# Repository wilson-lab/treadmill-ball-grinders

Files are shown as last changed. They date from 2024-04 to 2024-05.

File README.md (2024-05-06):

Treadmill Ball Grinders
===

**In progress: versioned documentation for ease of sharing.**

## Spherical Treadmill Fabrication

### Materials
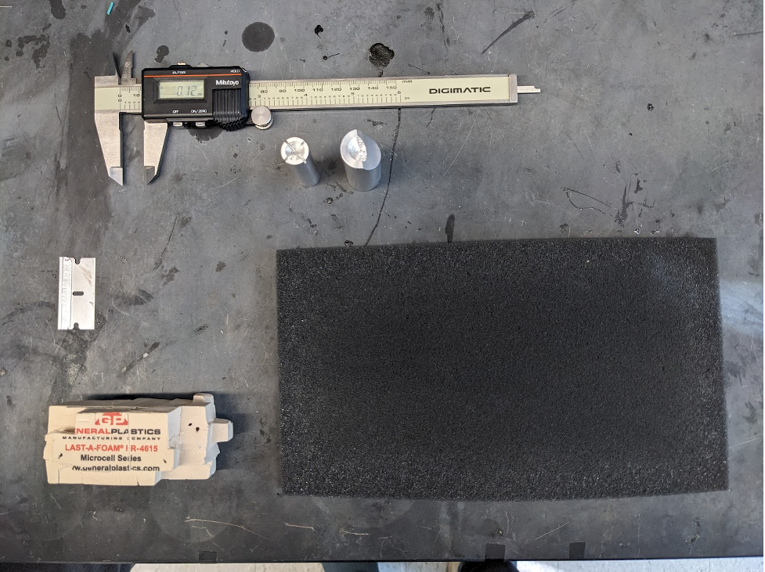
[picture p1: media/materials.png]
materials

* Foam - FR-4615 from General plastics
* Razor blade
* 'Coarse' and 'fine' foam sphere grinders
* Calipers capable of tenths of milimeters
* Soft foam pad
* Ball holder and air regulator
* Black paint or a paint pen (optional)
* Snugly fitting gloves (optional)
* Face mask (optional)

### Notes
* Wearing gloves can be helpful to avoid pressing oils from your fingers into the ball, which make the ball harder to grind.
* Wear a face mask to avoid breathing in the dust as you grind, and wipe up excess foam afterwards.

### Fabrication Steps
1. **Cut a cube foam starting matrial.** Cut a cube (carefully) of the FR-4615 foam that is around ~11mm on each side using a razor blade.
	* It can be helpful to mark out the edges with a fine-tipped marker first, then cut into them (the marks will be ground away before the end).
1. **Trim the cube of foam.** Using the razor blade, trim down the sharp edges and corners of the cube to make it more spherical (e.g. the way you might peel a grapefruit's skin). 
	* Doing more of this trimming into a spherical shape here will make the next step easier. You should get a sense for it as you try the next step if you’ve done enough.
1. **Begin grinding the trimmed cube.** Place the trimmed material into the coarse (bigger) grinder that has a diameter of ~11.5 mm and start grinding down the cube. To do this:
	* Place the ball in the “cup" of the grinder and then grind it down by rolling it “away” from you with your thumb and forefinger. Apply enough force for the grooves in the cup to cut away the edges of the ball.
	* The initial grinds as the cube molds into a sphere require more force, and you will notice big chunks chipping off the foam.
	* You can roll it a bit to remove material, then take it out, rotate it a bit, and do it again on another face. It will eventually become much easier to move as it becomes more sphere-like. 
	* As the cube transforms into a sphere, use gentle force to avoid big chips that can leave deep dents or compress the foam.
	* Continue massaging the ball into the metal grinder while continuously moving the ball around to allow for all surfaces to get shaved down evenly. Keep doing this until hardly any material is being taken away and the ball appears smooth.
	* You’ll need to periodically knock the dust out of the grinder, so it ends up being: roll a bit, knock out the dust, rotate ball position, roll a bit… and so on.
1. **Grind the sphere to near its target size.** Move to the smaller spherical grinder when the ball is ~9.2 mm diameter and fits into the fine (smaller) grinder. 
	* Continue massaging the ball to allow for even shaving across the entire surface of the sphere. 
	* When the ball is close to its final size, switch to rolling the ball around on the surface of the soft foam pad. Keep the ball secured in the metal grinder, but be careful, the ball may jump off the foam. Note this step is to help ensure the ball finishes with very even shaving.
1. **Test ball performance as you finish grinding**. As the ball gets closer to 9mm start putting the ball on the ball holder with ~50-100mL/min of air and watching its behavior. 
	* The final diameter of the ball is ~9mm, _but we recommend starting to test when it is slightly larger to avoid overshooting._ 
	* Guidelines for what to look for when the ball is levitating on the air cushion:
		* The ball should fit snugly in the ball holder and bob gently.
		* The ball should not wobble from side to side, this indicates the ball is too small.
		* The ball should spin freely in circles when nudged with a feather, this indicates there is no friction from the holder.
	* The ball might pass all the check points, but ultimately the flies must decide if they like it or not.
1. **(optional) Add markings to the ball for tracking** Once the ball is the final desired size, use the black acrylic paint or paint pen to mark the surface of the ball for behavioral tracking (e.g. a camera and FicTrac)
	* Ensure that every view angle of the ball has a unique pattern on it.
	* Numbers and letters are generally good, or spots of different sizes and shapes. 
	* Sharpie will also work for marking the ball but will have much less contrast under IR compared to the black paint. 
	* NOTE: if you grind the ball down after applying the markings, you will smear them and reduce the contrast.

## Grinders

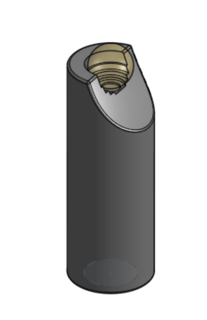
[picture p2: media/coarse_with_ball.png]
coarse


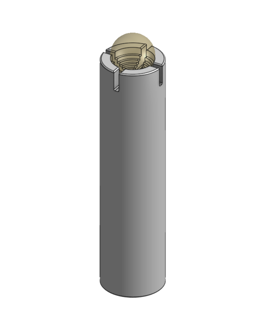
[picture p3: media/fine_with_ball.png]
fine


### Grinder Fabrication

There are two components to be machined, a 'fine' and 'coarse' grinder. They were made to be CNC machined with a lathe. So far they have been outsourced to Protolabs with good results. Using Aluminum 6061-T651 with "Edges broken (tool marks visible)” works well.

It is possible they’d work as 3D printed plastic (at reduced cost) but this has not yet been tested.

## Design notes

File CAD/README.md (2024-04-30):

CAD Files
===
Standard CAD files for each version are exported from onshape (where they are versioned).

STL files are exported with units as mm (unless specified otherwise), and 'fine' resolution. As of 2024 this means angular deviation 2.5 deg, and chordal tolerance of 0.06 mm.

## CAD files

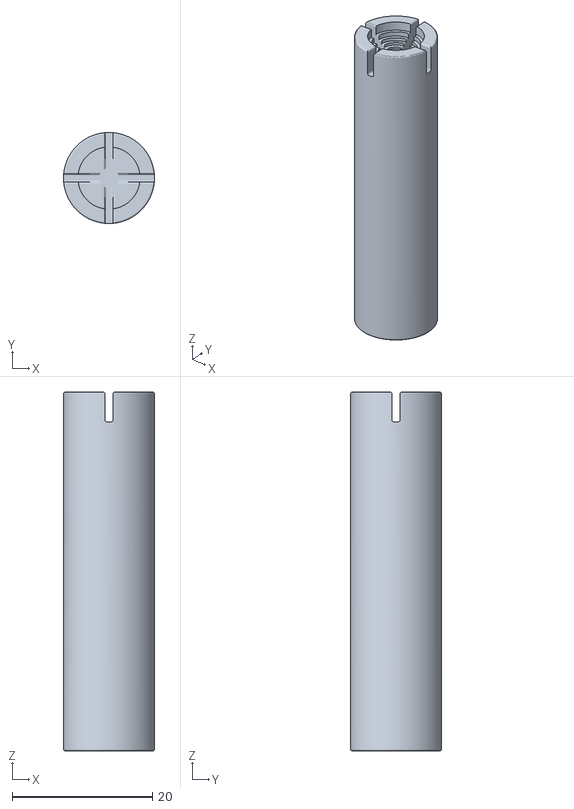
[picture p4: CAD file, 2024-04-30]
CAD/versions/v0.1/9mm-fine-grinder_mm.stl
13.0 x 13.0 x 51.2

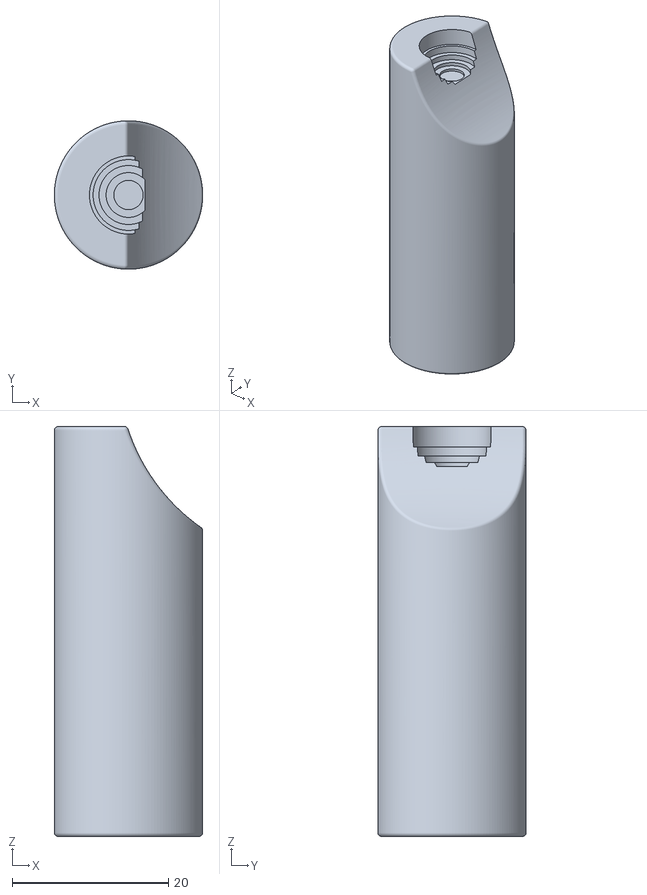
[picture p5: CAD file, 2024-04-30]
CAD/versions/v0.1/9mm-coarse-grinder_mm.stl
19.0 x 19.0 x 52.5

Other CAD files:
CAD/versions/v0.1/9mm-coarse-grinder.sldprt
CAD/versions/v0.1/9mm-fine-grinder.sldprt
